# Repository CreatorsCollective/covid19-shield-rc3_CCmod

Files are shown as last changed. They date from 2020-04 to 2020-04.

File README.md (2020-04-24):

# covid19-shield-rc3_CCmod
Eine angepasste Version des original Prusa-RC3 Gesichtsschild-Bügel. Der Vorteil liegt in der guten Stapelbarkeit durch eine spitz zulaufenden Unterkanten.

## Dateien
Es sind drei Dateien vorhanden:

### 1. Der modifizierte Bügel


Gegenüber des original Prusa RC3 Bügels wurden ein paar Anpassungen gemacht.
- Modifikation der Höhe:

Der modifizierte Bügel ist 16,2mm statt 20mm hoch. Die Höhe ist immer noch komfortabel aber reduziert die Druckzeit.
- Entfernen des Logos:

Das Drucken einer Schrift oder Gravur erhöht die Anforderungen an den Drucker und erhöht auch die Druckzeit etwas. Daher wurde jegliches Logo entfernt
- Fasen

Fasen an Ober- und Unterkante erhöhen die Ergebnisqualität. Die Fase an der Oberkante ist ebenfalls für die "Sollbruchstelle" bei gestapelten Modellen zuständig
- Drucken ohne Stützen

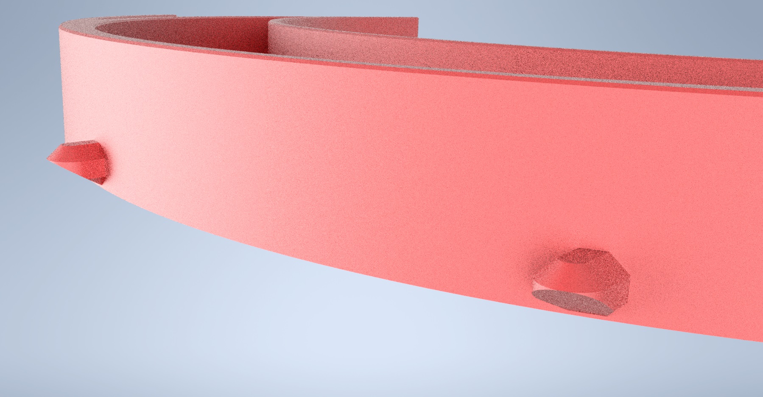
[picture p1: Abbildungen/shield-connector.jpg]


Die Nippel zum Einhängen der Lochfolie wurden nach unten hin gefast. Dadurch können auch gestapelte Versionen ohne Stützstruktur gedruckt werden

### 2. Das Verbidungselement
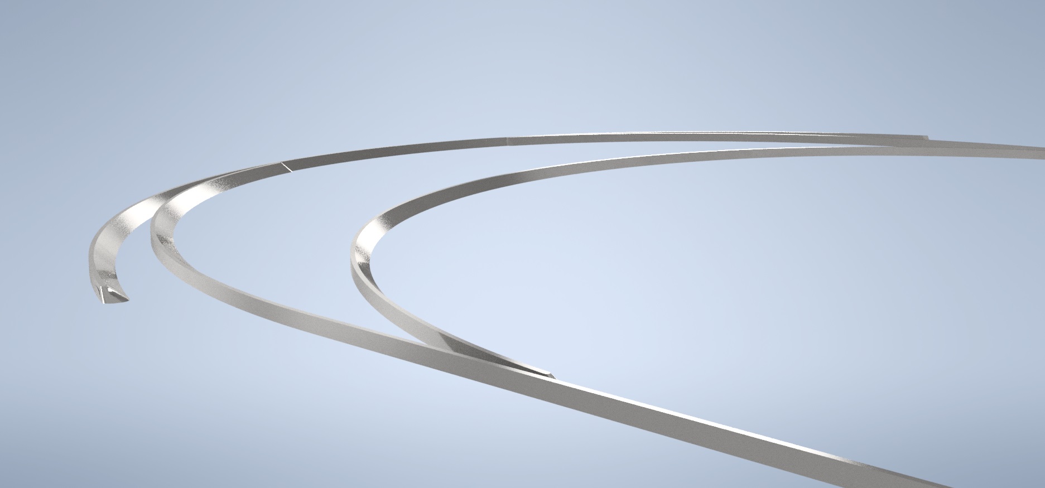
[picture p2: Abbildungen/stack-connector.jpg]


Ein zusätzliches Verbindungselement liegt bei, damit die Bügel bei einer Druckschichthöhe von 0,3mm gut gestapelt werden können. Dieses Verbdindungselement kann immer direkt auf die Oberkante eines Bügels gelegt werden und das nächste Modell direkt drüber gesetzt werden. Das "Spitz-Zulaufen" erreicht an der dünnsten Stelle 0,5mm Stärke was eine durchschnittliche Breite einer einzigen 3D-Druckbahn entspricht. Damit sind die gestapelten Bügel nur durch eine Bahn miteinander verbunden. Funktioniert bei meinen Tests bisher sehr gut. Die Höhe von 1,8mm ist dem geschuldet, dass die Schräge nicht zu steil sein darf für ein Stützstruktur-freies Drucken.

### 3. Eine fertige Stapelversion
Eine fertige Stapelversion ist auch beigelegt. Hier sind 8 Bügel aufeinandergestapelt. Die Bügel sind 16,2mm, das Verbindungselement 1,8mm. Zusammen wiederholen sie sich also jede 18mm.

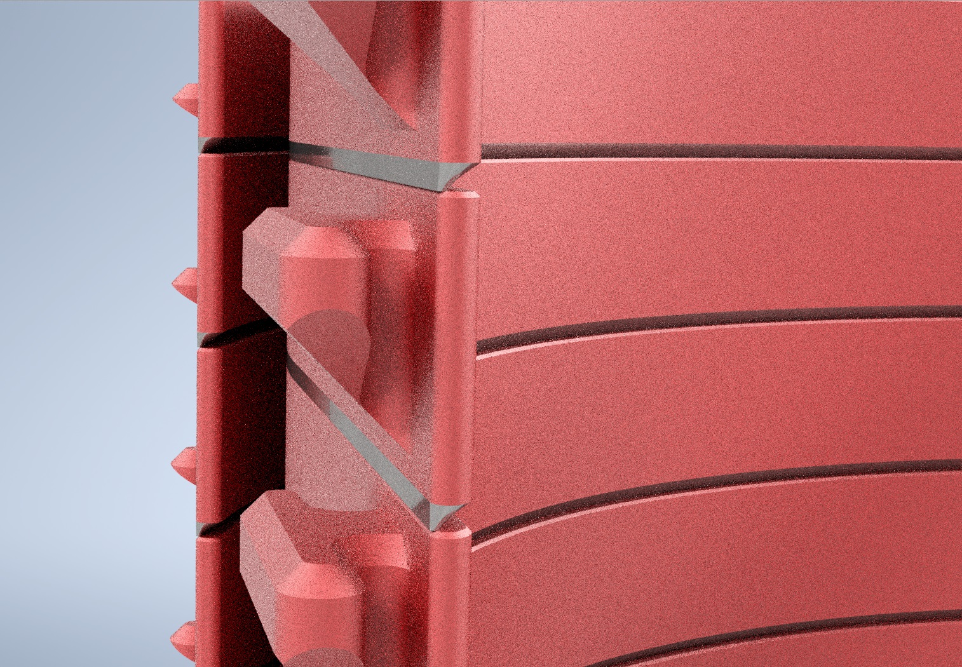
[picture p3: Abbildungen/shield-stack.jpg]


## Ablösen der gestapelten Modelle
Am einfachsten lassen sich die gestapelten Modelle durch kleine Einschnitte ermöglichen, wie es in den folgenden Abbildungen gezeigt ist.

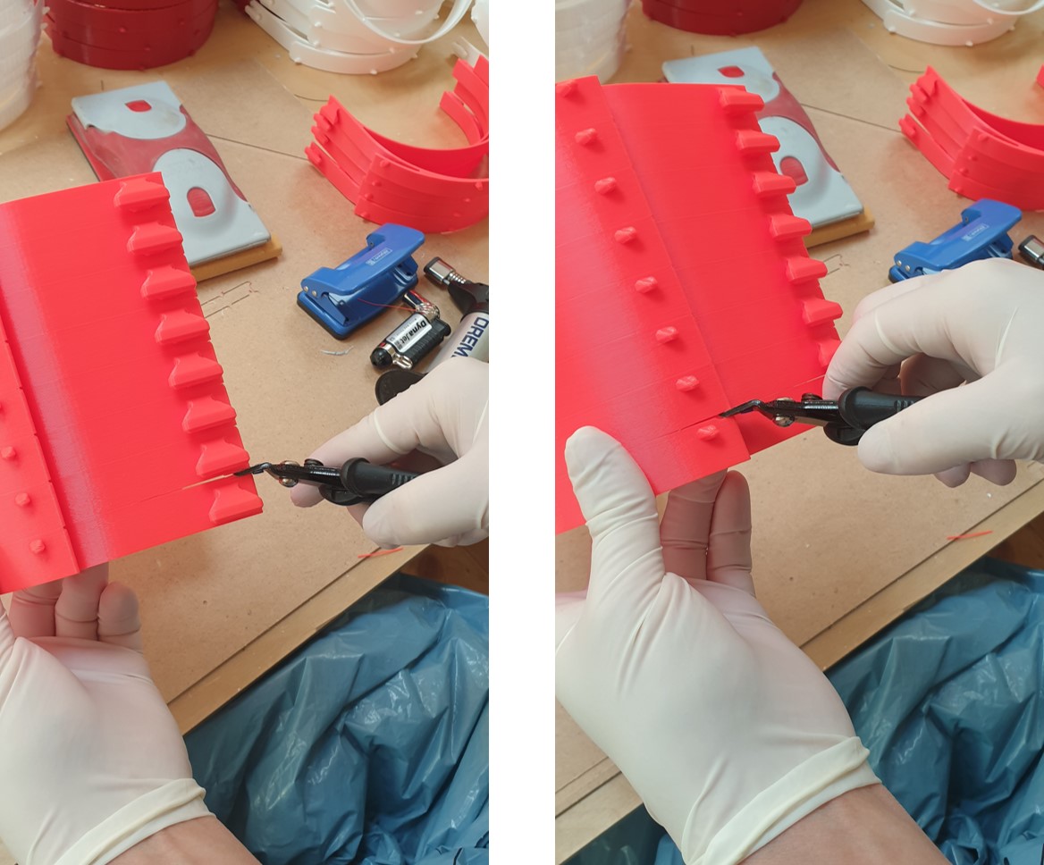
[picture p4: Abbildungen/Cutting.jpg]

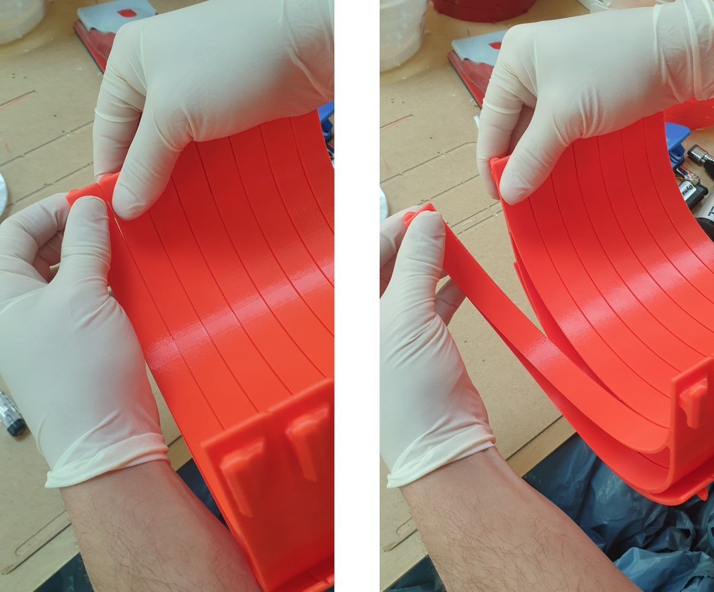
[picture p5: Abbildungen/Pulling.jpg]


## Wichtige Hinweise
Das Modell funktioniert vor allem mit folgenden Druckparameter:
- Schichthöhe: 0,3mm (Wichtig, da sonst die Verbindungen auf der falschen Schicht beginnen und damit die Sollbruchstelle nicht gewährleistet ist)
- infill: 10-15% reicht

Darüber hinaus kann auch ich keine Gewährleistung für die Funktion geben. Das Nutzen geschieht auf eigene Gefahr und nach eigenem Ermessen. 

Das 3D-Modell kann nach Belieben verändern und genutzt werden. Der Entwurf steht unter Lizenz: [Creative Commons (4.0 International License)](https://creativecommons.org/licenses/by-nc/4.0/)
Die Original-Datei Prusa RC3 stammt von [PrusaResearch](https://www.prusaprinters.org/prints/25857-prusa-protective-face-shield-rc2/files)

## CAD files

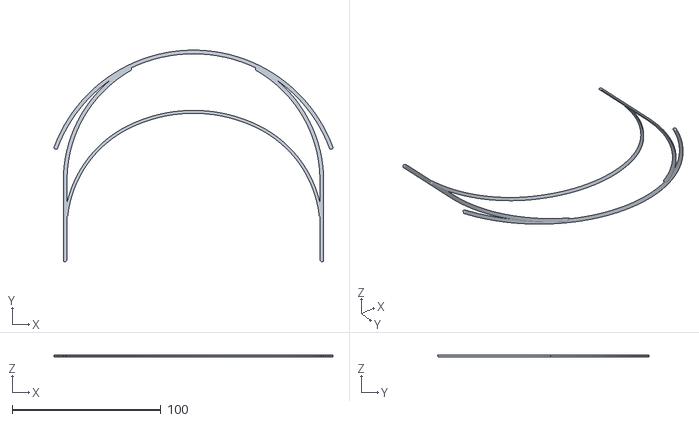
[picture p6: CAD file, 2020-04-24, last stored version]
covid19-shield_rc3_CCmod_v4_Verbindung.stl
187.6 x 142.3 x 1.50

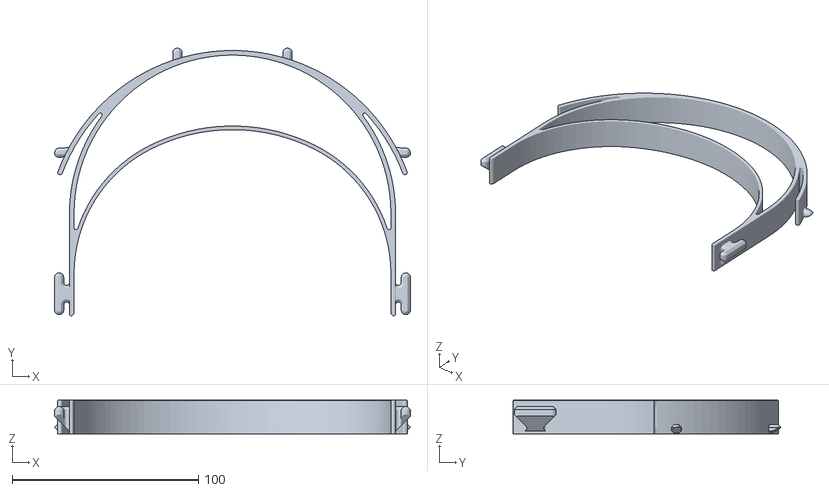
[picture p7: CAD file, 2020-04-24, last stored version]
covid19-shield_rc3_CCmod_v4.stl
191.0 x 143.6 x 18.0
